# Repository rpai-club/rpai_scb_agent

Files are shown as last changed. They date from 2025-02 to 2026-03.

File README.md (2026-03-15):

# Cross Point Project
Software-Configured Breadboard Hardware Targeting Circuit Wiring Error Reduction in ECE Labs.
#
Abstract:
#
The hardware project aims to examine the effectiveness of software-configured wiring compared to traditional manual wiring of breadboards. While both methods use actual hardware, the software-configured approach automates the connections between components, thereby minimizing wiring errors and setup time. The intent is to investigate the impact of each approach on student comprehension, engagement, and error rates. By comparing these two approaches, the project seeks to determine which method better supports student engagement, educational outcomes and reduces frustration associated with complex circuit construction.
#
Introduction:
#
Hands-on experiential learning is a cornerstone of ECE education, typically relying on manual wiring of circuits on solderless breadboards. Using a traditional solderless breadboard as the means for building electronic circuit lab experiments requires the student, in addition to placing components, to manually insert wires to connect together the component pins according to a schematic diagram. These manual translation steps from schematic to hardware can lead to wiring errors in the experimental setup that can obscure circuit principles. While this manual wiring method offers valuable experience in physical component handling and troubleshooting, the extra time needed for debugging and correcting these errors leads to frustration and loss of precious lab time to investigate the circuit concept in question.

The goal is to evaluate the educational benefits and potential drawbacks of these software-configured hardware systems compared to traditional manual wiring. By doing so, it addresses the need for balancing hands-on skills with error minimization and conceptual understanding in electrical engineering education.
#
Analog switch matrix cross point experiment breadboard.
#
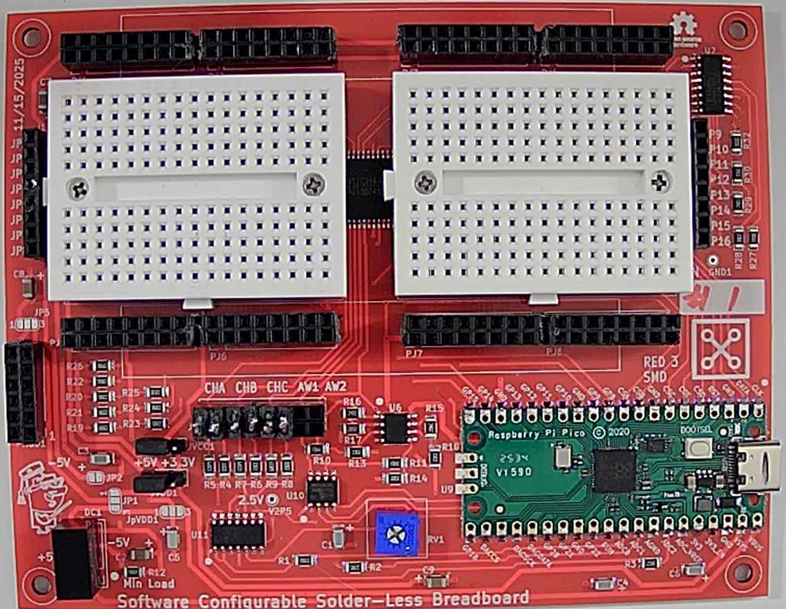
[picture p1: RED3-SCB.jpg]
Screenshot Prototype PCB

Production PCB (Red3 version, instructions for ordering boards can be found in PCB Projects folder)
 
The idea is to computerize the wiring of the breadboard in an effort to reduce student frustration when building complex experiments. Using four analog 16X8 cross point switches wired together into two 32X8 cross points with a fifth switch matrix interconnecting the two smaller arrays into effectively a single 64X16 array.

This breadboard makes real, hardware connections between the 64 breadboard component pins on the board to the16 “jumper” nodes on the board via software commands, instead of needing to manually install jumper wires. The prototype PCB is shown, figure 1, which incorporates two mini 170 pin solderless breadboards, one for each of the 32X8 cross point arrays. There are a combined 68 total component pin locations across both mini breadboards with power distribution strips top and bottom. The two mini breadboards connect to the PCB through pogo pins and so they can be easily removed. It would then be possible to bolt on custom daughter PCBs with whatever components are needed for a given course already installed. Such as CMOS transistor arrays (CD4007) with even some pre-wired sub-circuits like current sources and OTAs.

The combined 64X16 cross point matrix board uses a total of 5 CH446DS 16X8 analog cross point ICs (from China) programed via a RP-2040 micro controller breakout board (Pi Pico or equivalent). Materials cost per board, in quantities of 10 or more, is less than $30 not including the assembly labor.

The board is powered from the Pi Pico USB connection. For powering the experiment circuits, Jumpers can be configured for 0 and +3.3V, 0 and +5V or -5V and +5V power (or 0 and +10V) using an on board isolated 5V DC-DC generator.

LTspice is used to enter the schematic for the experiment. In addition to the standard library symbols a number of supporting schematic library files have been created. Schematic symbols for TO-92 transistors and resistors of various lead spacing are available in the LTspice files.

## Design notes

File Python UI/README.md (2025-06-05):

# Crosspoint Project interface for Universal-ALICE
Controling the Software Configurable Breadboard (SCB) hardware is built on top of the Universal ALICE hardware agnostic platform. 
#
Repository for the Python source code and hardware level specification files.
#
The main Universal ALICE GUI is written in Python (3.x) and depends only on the more or less generic standardly available Python plugin libraries (such as Tcl/Tk, numpy, pyplot etc.). The hardware specific interface level is also generally implemented in Python plus any plugin libraries (such as pyserial). The hardware specific interface for the SCB extends the Raspberry Pi Pico interface to include controls for reading LTspice .net or .cir formated netlists.

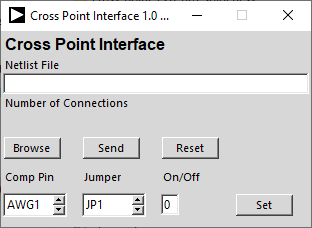
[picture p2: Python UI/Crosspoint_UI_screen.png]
Screenshot interfacescreen

Crosspoint Interface ALICE Screen

The Pi Pico board must be flashed with the corresponding firmware from the Arduino firmware folder.

If you are not a technical individual or highly familiar with computer operating systems and you have your choice of computers, a Windows computer is highly recommended. You will usually run into fewer issues, if any, with that operating system.

Known Issues: If your computer encrypts files saved on external storge devices (USB disk drives) then the UF2 Bootloader method of flashing firmware to micro-controller boards will not work. You would need to use a different computer that does not encrypt files or consult your local system administrator.

Linux Operating system: On Linux computers access to USB based serial comms devices may not be allowed for non root users by default. A udev rules file needs to be added. Place the 99-arduino.rules from this repository in etc/udev/rules.d

It contains one line per board / vendor:

SUBSYSTEMS=="usb", ATTRS{idVendor}=="2E8A", ATTRS{idProduct}=="000A", GROUP="dialout", MODE="0666"

If this rules file does not work on your version of Linux there may be other things like this that work. Searching the web on how to make serial USB devices work may provide an alternate solution or consult with your local Linux expert.

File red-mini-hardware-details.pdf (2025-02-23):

## Red Mini Hardware Construction (revised 1/20/25):

Analog switch matrix cross point experiment breadboard.

The idea is to computerize the wiring of the breadboard in an effort to reduce student frustration when building complex experiments. Using four analog 16X8 cross point switches wired together into two 32X8 cross points with a fifth switch matrix interconnecting the two smaller arrays into effectively a single 64X16 array.

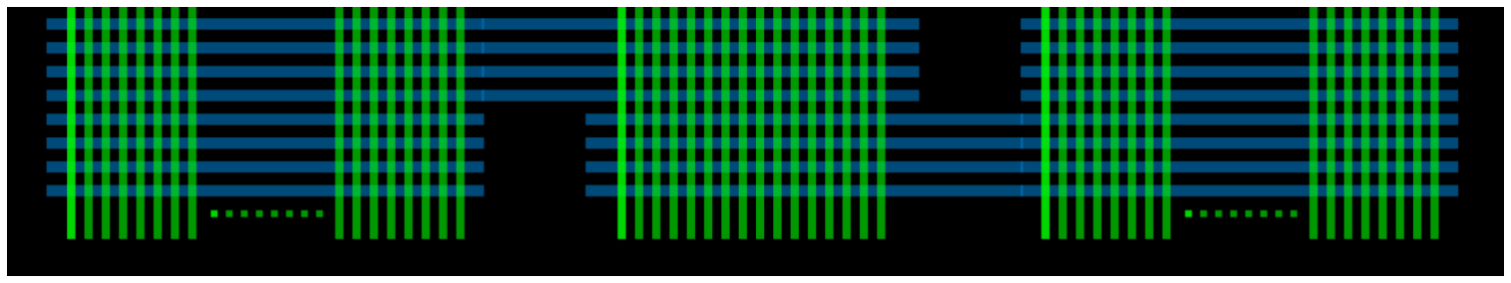
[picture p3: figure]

This breadboard makes real, hardware connections between the 64 breadboard component pins on the board to the16 “jumper” nodes on the board via software commands, instead of needing to manually install jumper wires. The prototype PCB is shown, figure 1, which incorporates two mini 170 pin solderless breadboards, one for each of the 32X8 cross point arrays. There are a combined 68 total component pin locations across both mini breadboards with power distribution strips top and bottom. The two mini breadboards connect to the PCB through pogo pins and so they can be easily removed. It would then be possible to bolt on custom daughter PCBs with whatever components are needed for a given course already installed. Such as CMOS transistor arrays (CD4007) with even some pre-wired sub-circuits like current sources and OTAs.

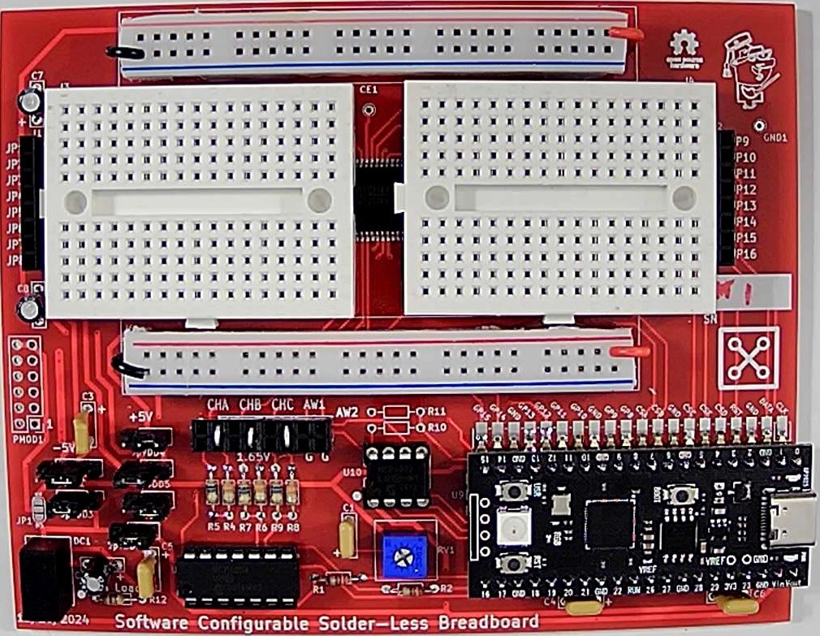
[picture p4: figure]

Figure 1, Prototype PCB.

The combined 64X16 cross point matrix board uses a total of 5 CH446DS [2] 16X8 analog cross point ICs (from China) programed via a RP-2040 micro controller breakout board (Pi Pico[3]
or equivalent).
Materials cost per board, in quantities of 10 or more, is less than $30 not including the assembly labor.

The board is powered from the Pi Pico USB connection. For powering the experiment circuits, male Pin Jumpers can be set for 0 and +3.3V, 0 and +5V or -5V and +5V power (or 0 and +10V) using an on board isolated 5V DC-DC generator.
LTspice[4]
is used to enter the schematic for the experiment. In addition to the standard library symbols a number of supporting schematic library files have been created, figure 2. Schematic symbols for TO-92 transistors and resistors of various lead spacing have been created. There are also example schematic symbols with the proper pin spacing for 8, 14 and 16 pin DIP packages. The standard library components can of course also be used.

The library schematics for the switch matrix connections contain 60 Ω resistors and 16 pF capacitors which model the analog switch. One end of a matrix switch will have the component pin net and the other end will have one of the 16 "jumper" nets (JP1-16).

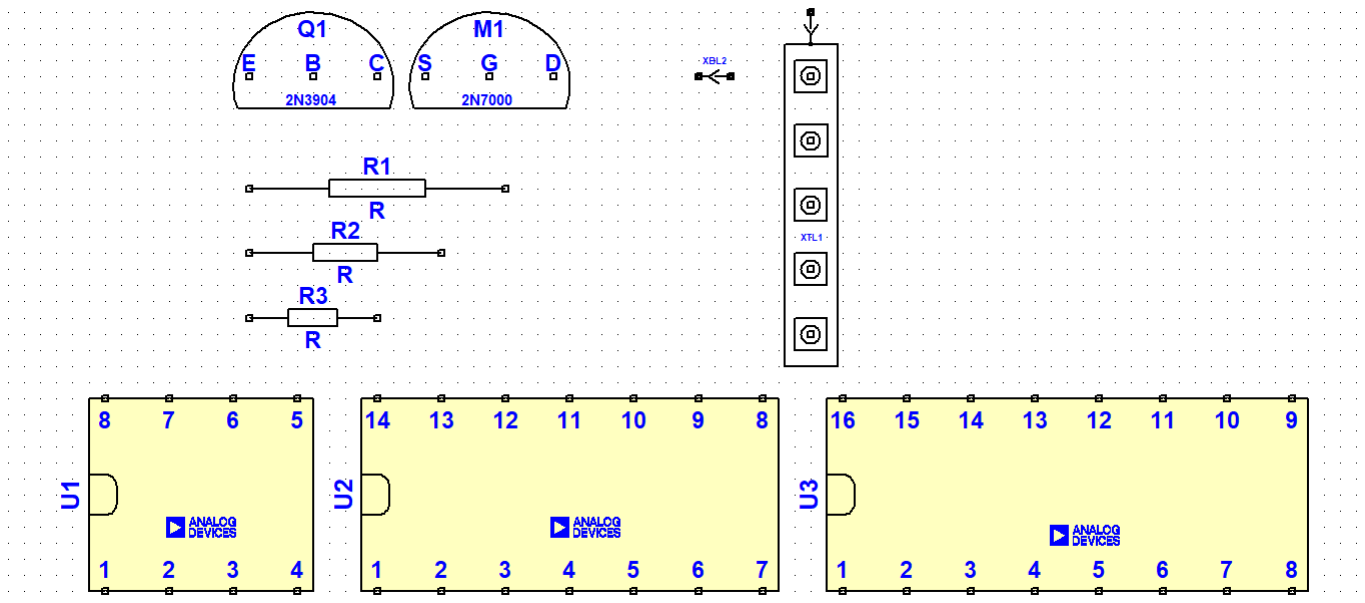
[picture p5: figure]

Figure 2, Schematic symbols.

A floor planning schematic template, figure 3, has been created to help the user figure out where to place the parts on the left and right side mini breadboards and then use the "jumpers" to wire them together. There is a schematic symbol for each breadboard column (the 5 pins shorted together). Each breadboard column has a specific name based on its location. Names are numbered from 1 to 17 starting with the top left section, TL1-17, then the bottom left section, BL1-17, then the top right section TR1-17, and finally the bottom right section, BR1-17.

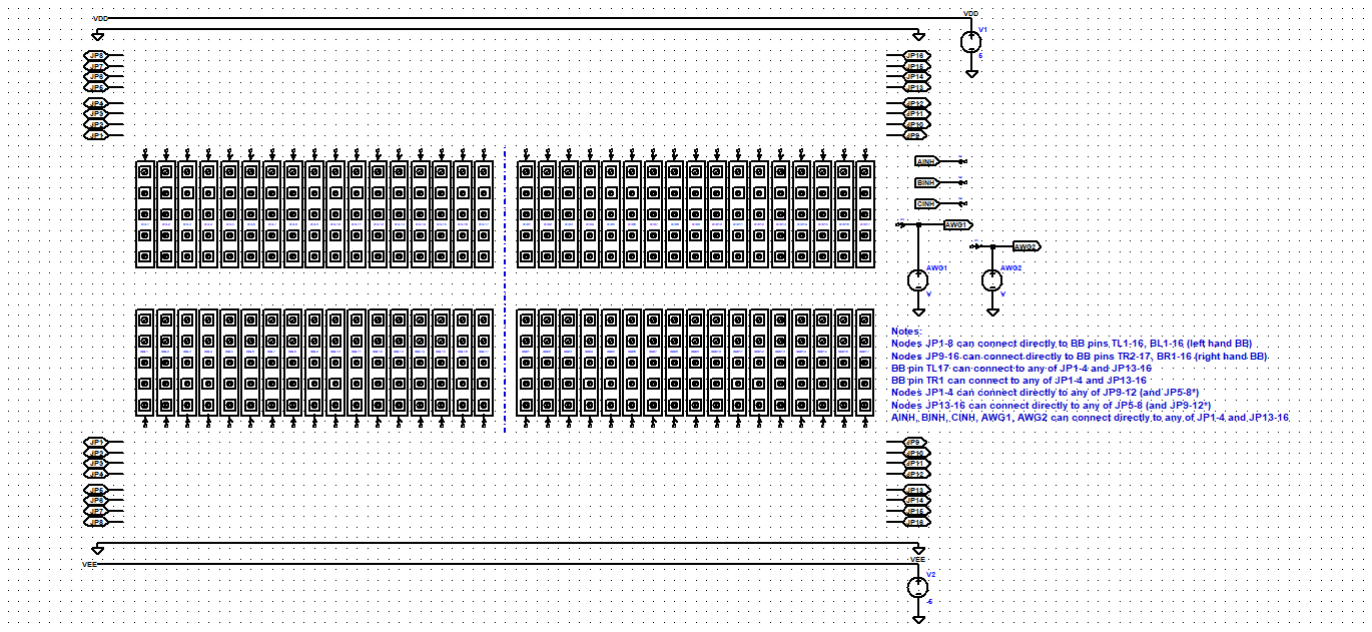
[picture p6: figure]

Figure 3, LTspice floor planner template schematic

In figure 4 we see an example circuit of a transistor level op-amp that has been floorplanned and interconnected with the JP jumper nets. Components can also be connected between a column pin and one of the top and bottom power and ground rails simply by a wire.

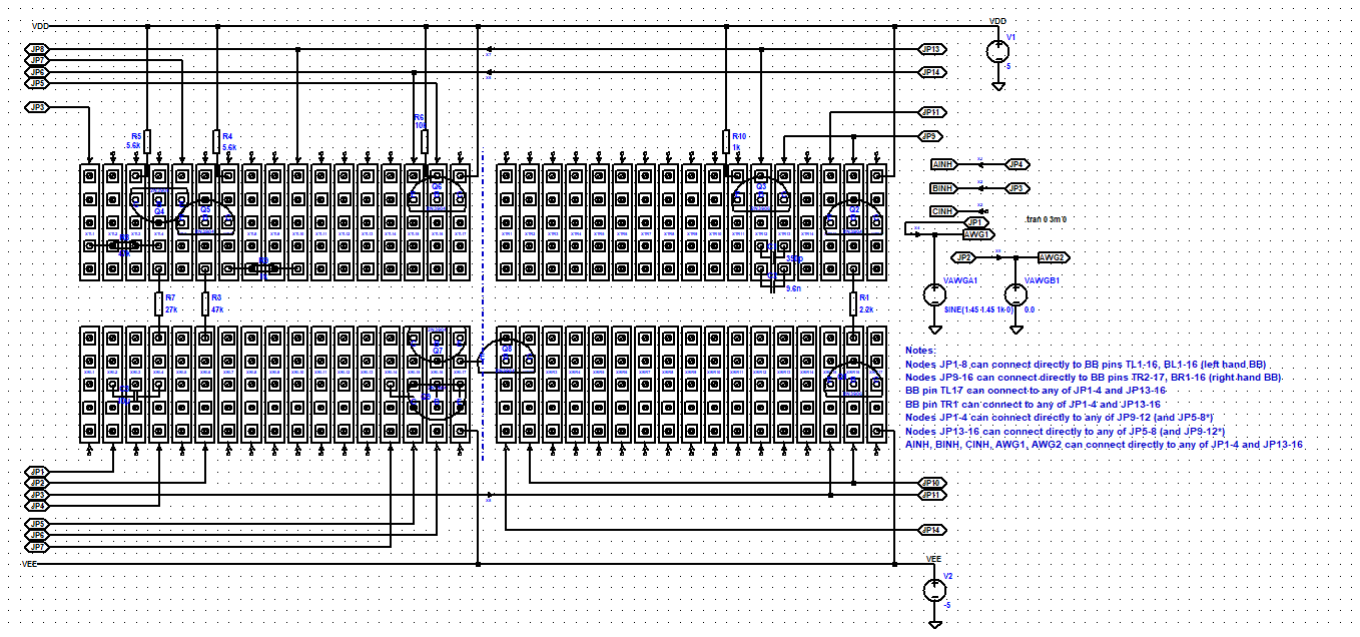
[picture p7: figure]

Figure 4, Example floor planned circuit

There is also a way to draw the circuit as a more conventional schematic, figure 5. The same op-amp circuit has been redrawn using standard symbols from the LTspice library with the addition of single switch interconnection symbols. The little pointy arrow symbols are placed in series with certain nets to indicate the component locations on the breadboard. These interconnection symbols are again named based on the BB holes (TL1-17, BL1-17, TR1-17, BR1-17) the parts are plugged into. This approach is easier to visualize the circuit as a schematic but perhaps harder to floor plan where to place the devices.

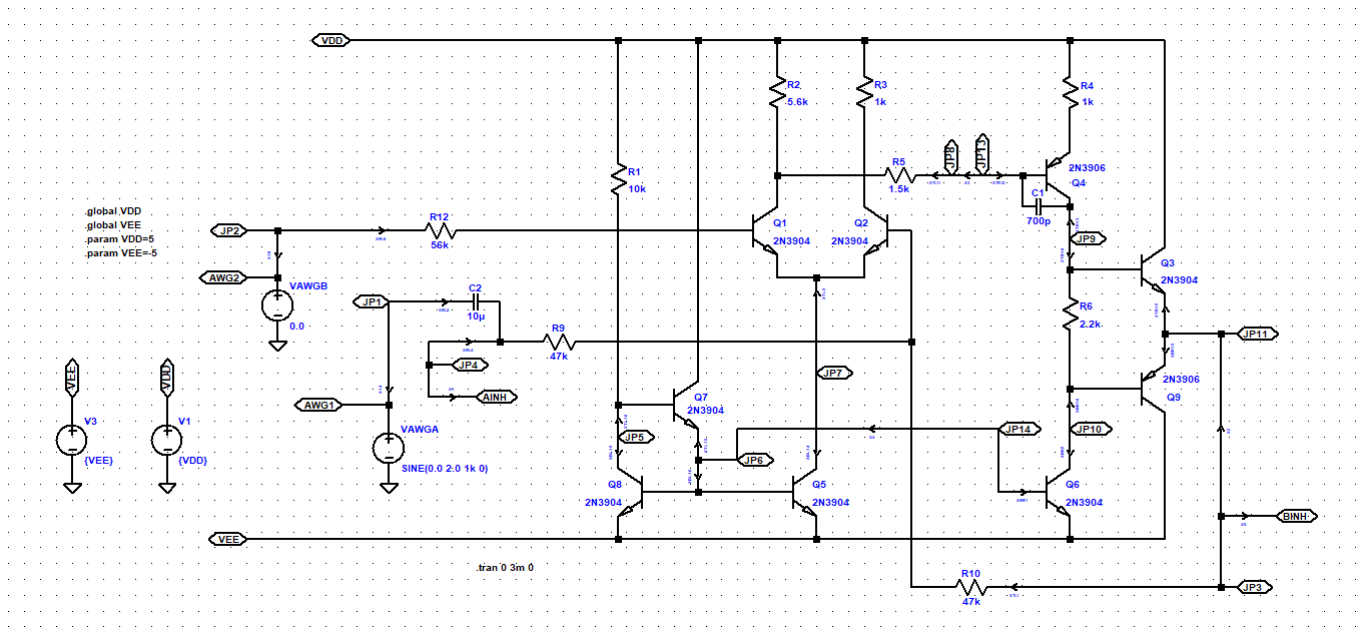
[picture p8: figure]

Figure 5, Conventional Schematic method

Correct simulation results insure that you have it all wired correctly before moving to the actual hardware.

A Python script looks through the saved LTspice .cir net list file looking for sub circuits starting with XX in their names. Then parses the connections based on the names (based on breadboard pin locations, TL1-17, BL1-17, TR1-17, BR1-17) and JP1-16 to send commands to the Pi Pico and on to the cross point switches. Everything else is ignored.

As long as you follow these rules when building the schematic the process is simple and mostly automatic. Programming the board is done through ALICE Universal[5]
using a hardware specific
interface configuration file for this cross point prototype including a way to turn on and off matrix switches manually as well.

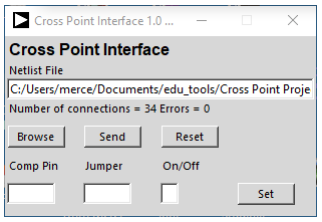
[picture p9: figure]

Cross Point Matrix control user interface The following are a few additional example circuits built using the breadboard.
The LTspice schematic in figure 6 was used to configure four CD4007 transistor arrays as a ring oscillator consisting of 11 CMOS inverter stages. It uses 56 of the 68 possible device pins and all 16 of the jumpers of the switch matrix. Manual jumper wires are used to connect each of the DIP (pins 7 and 14) ground and power pins to the power and ground rails on the board. All other connections are programed by the netlist.

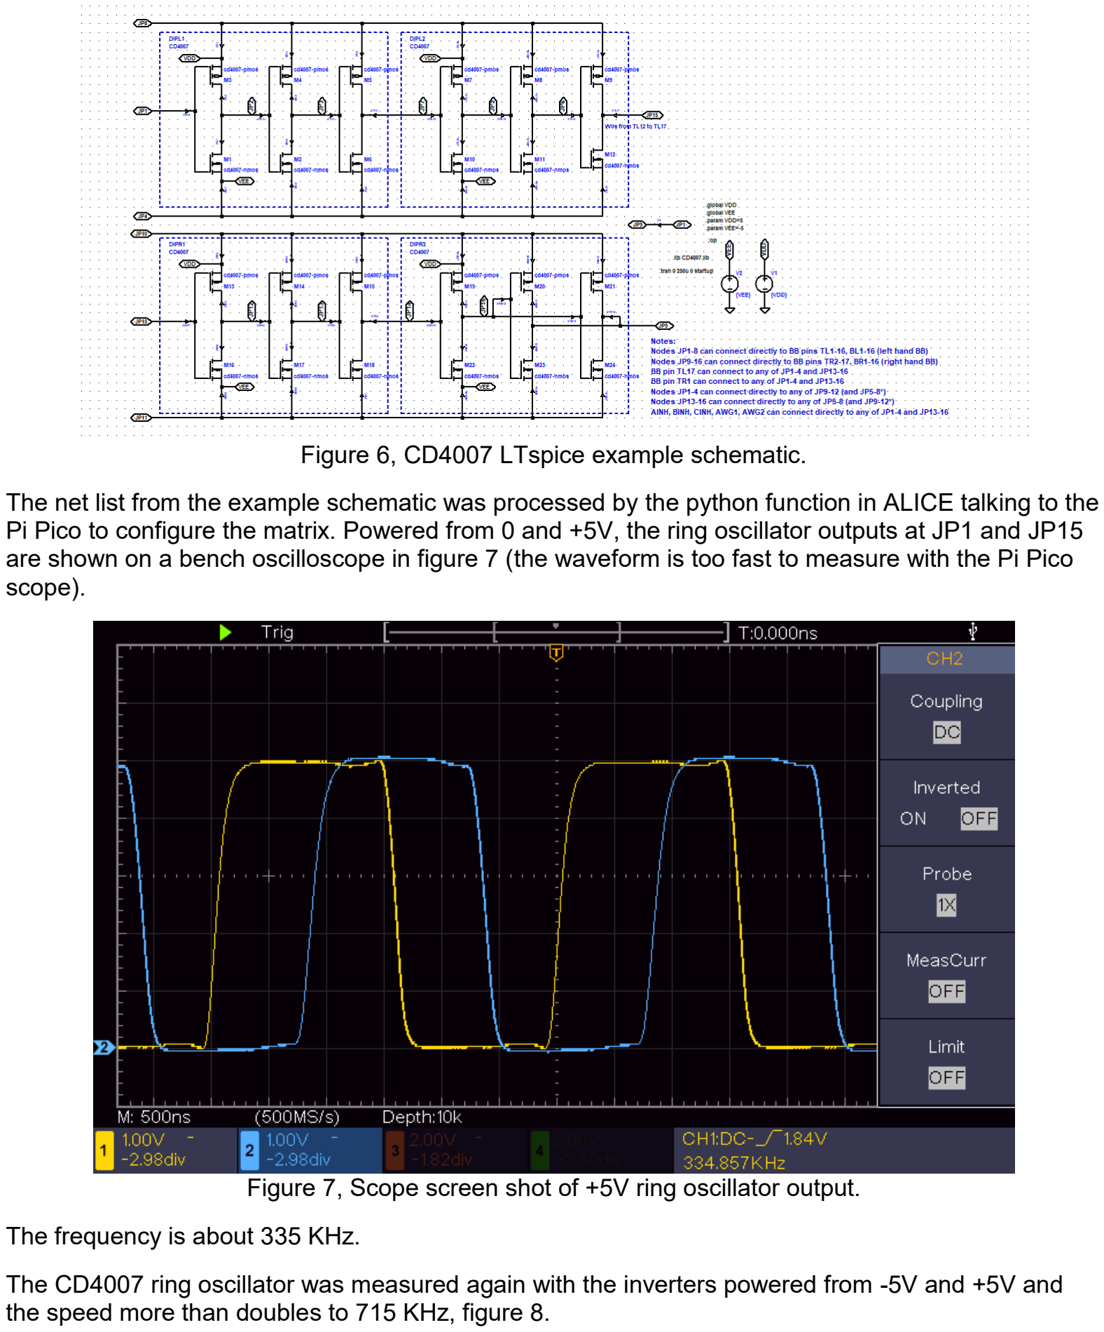
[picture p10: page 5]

Figure 6, CD4007 LTspice example schematic.

The net list from the example schematic was processed by the python function in ALICE talking to the Pi Pico to configure the matrix. Powered from 0 and +5V, the ring oscillator outputs at JP1 and JP15 are shown on a bench oscilloscope in figure 7 (the waveform is too fast to measure with the Pi Pico scope).

Figure 7, Scope screen shot of +5V ring oscillator output.

The frequency is about 335 KHz.

The CD4007 ring oscillator was measured again with the inverters powered from -5V and +5V and the speed more than doubles to 715 KHz, figure 8.

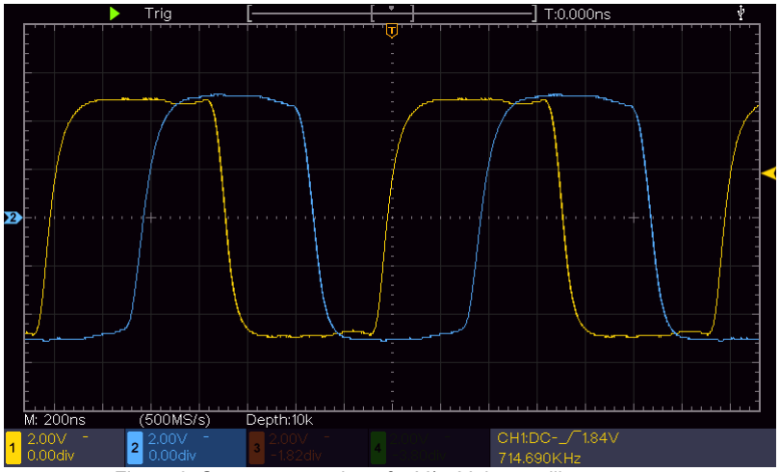
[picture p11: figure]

Figure 8, Scope screen shot of -5V/+5V ring oscillator output.

A Schmitt trigger relaxation oscillator can be constructed from the CD4007 CMOS transistor level inverters, figure 9. The Schmitt trigger is made by rearranging the connections and adding resistor R1 and Capacitor C1 to set the frequency. The M1,3 and M7,10 inverters are stronger than the other 4 inverters because their sources are connected directly to VDD and VEE rather than through the 60 Ω switch resistances. A “strong” inverter and a “weak” inverter are connected as a latch. This latch action determines the high and low threshold of the Schmitt trigger.

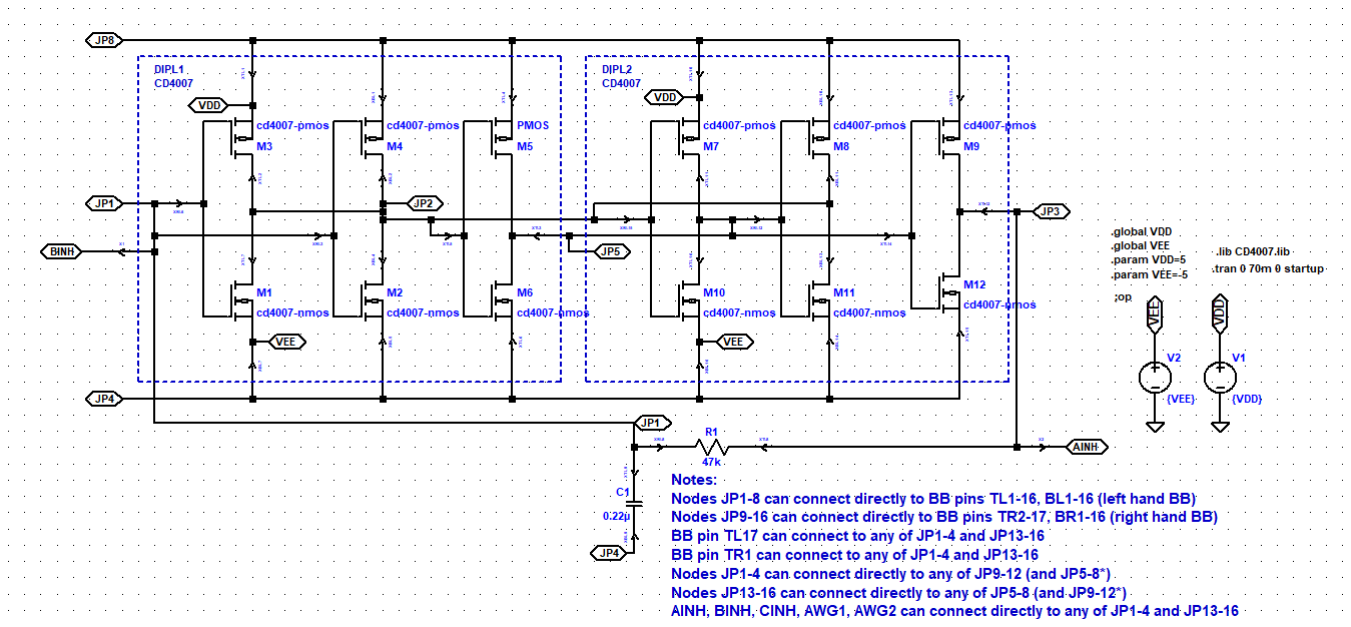
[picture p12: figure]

Figure 9, CMOS inverter relaxation oscillator.

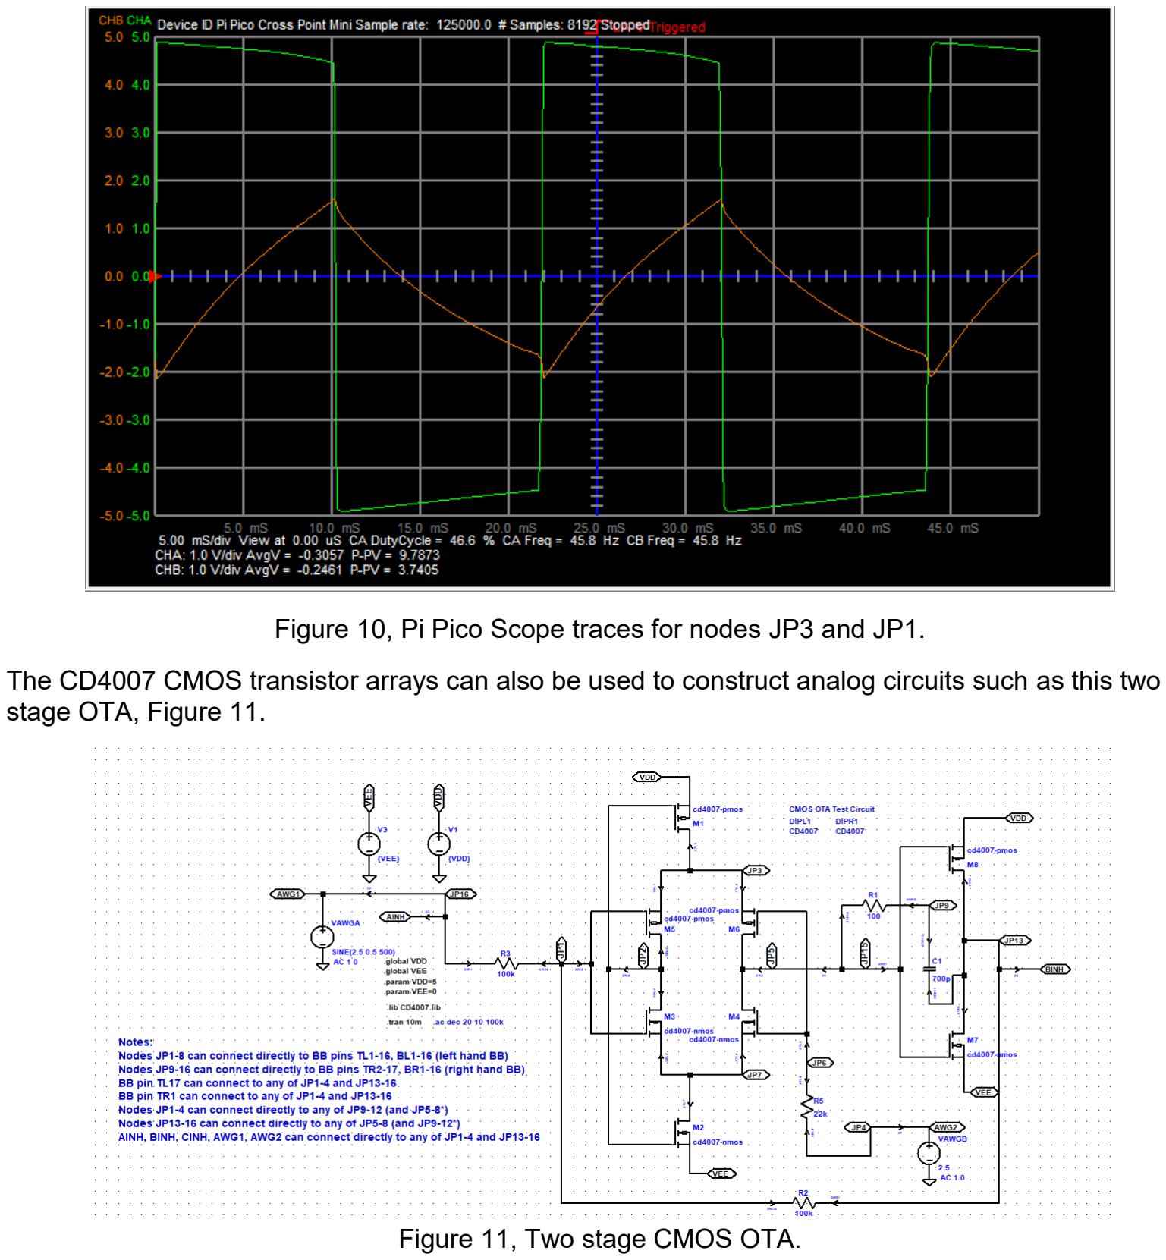
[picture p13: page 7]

Figure 10, Pi Pico Scope traces for nodes JP3 and JP1.

The CD4007 CMOS transistor arrays can also be used to construct analog circuits such as this two stage OTA, Figure 11.

Figure 11, Two stage CMOS OTA.

References:

[1] Jumperless breadboard product, https://www.tindie.com/products/architeuthisflux/jumperless/ , https://github.com/Architeuthis-Flux/Jumperless
[2] CH446DS1 datasheet, https://www.wch-ic.com/downloads/CH446DS1_PDF.html
[3] Pi Pico, https://www.digikey.com/en/products/detail/raspberry-pi/SC0915/13684020?utm_adgroup=&gad_source=1 (https://www.digikey.com/en/products/detail/raspberry-pi/SC0915/13684020?utm_adgroup=&gad_source=1)
[4] LTspice, https://www.analog.com/en/resources/design-tools-and-calculators/ltspice-simulator.html
[5] ALICE Universal, https://github.com/damercer/Universal-ALICE

Construction order of operations:

The order of assembly operations is first to install all the components that are soldered using hot air.

The first things requiring solder paste and hot air to install on the board are the pogo pins. Add a small dollop of solder paste in each pogo pin hole. Then insert a pogo pin (spring end up) in each hole. Using hot air reflow the solder paste until each pin flows down level into its hole.

The second things to install are the CH446DS quad flat pack ICs. Apply a small amount of solder paste along the four sides of the footprint. Using a conventional soldering iron melt the solder paste and “tin” the PCB lands with small mounds of fresh solder. The correct amount of solder will generally be left behind on each pin as the soldering iron is slowly dragged across the PCB.

Note the small white dot on the PCB near the lower left of each footprint on the PCB. This needs to be aligned with the dot on the IC package. It is a good idea to have all five of the packages properly aligned / orientated before hand. Mount the ICs one at a time. Using the hot air heat each IC footprint until the solder starts to melt. Using tweezers pick up the IC package, remembering to keep the proper orientation with the white dot, and place it on the melted solder. The IC should self-align and float on the melted solder by surface tension. You may need to nudge the IC slightly with the tweezers depending on how close it was to the proper position when you placed it. Remove the hot air as soon as it looks aligned properly to not over heat the IC.

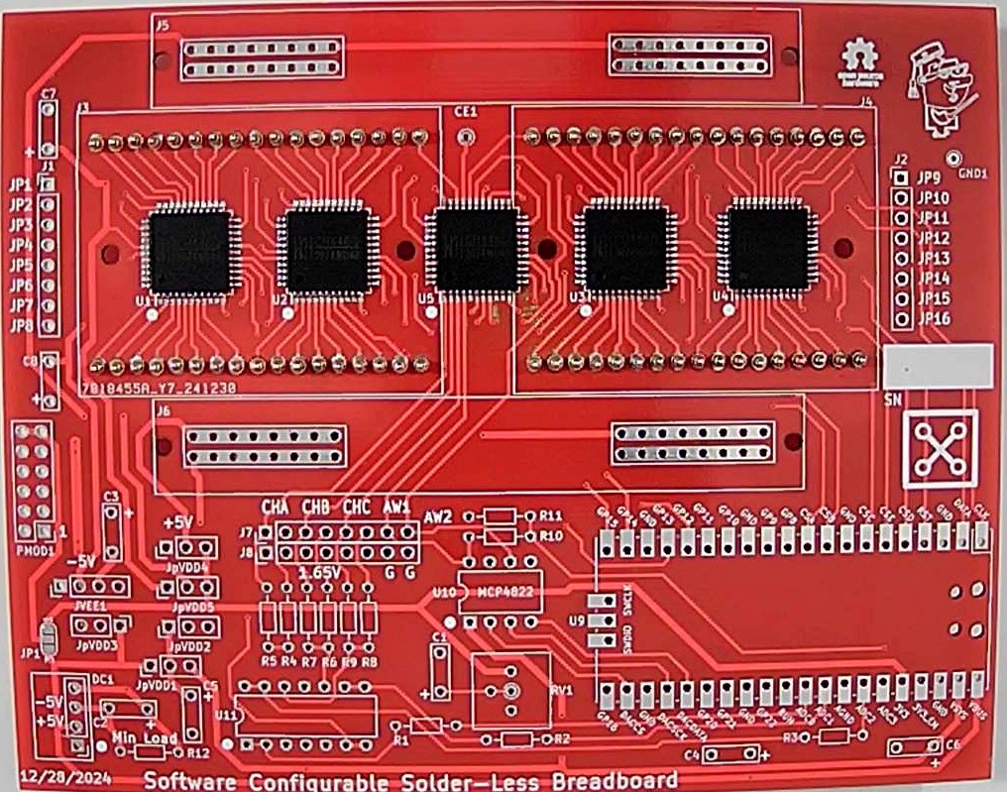
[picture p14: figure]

When installing the rest of the components which are through hole, it is best to start with the shortest devices (closest to the surface of the board). These would be the resistors. Then move to the next tallest etc. A small strip of masking tape can be used to temporarily hold the components tight to the board when you flip the board over to solder the leads from the bottom.

Additional Notes:

Software Configurable Solderless Breadboard Connections

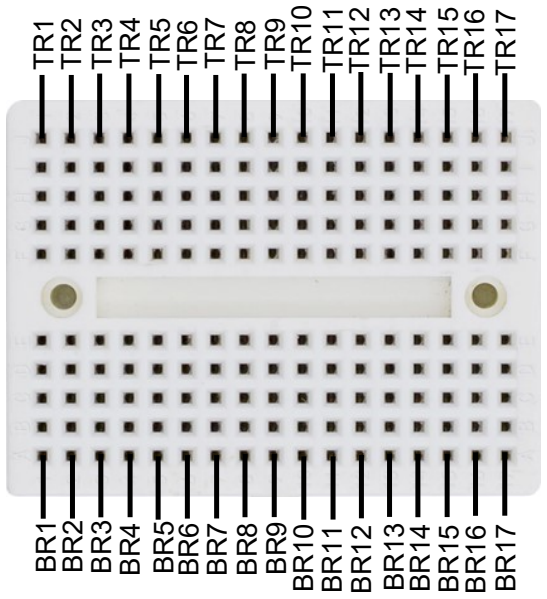
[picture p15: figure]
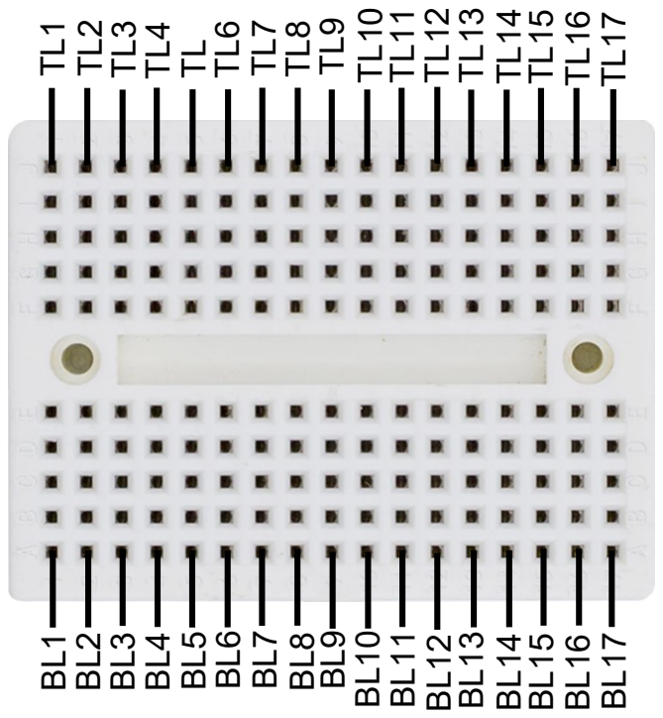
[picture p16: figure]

Mini Solderless Breadboard Pin Names (Red)

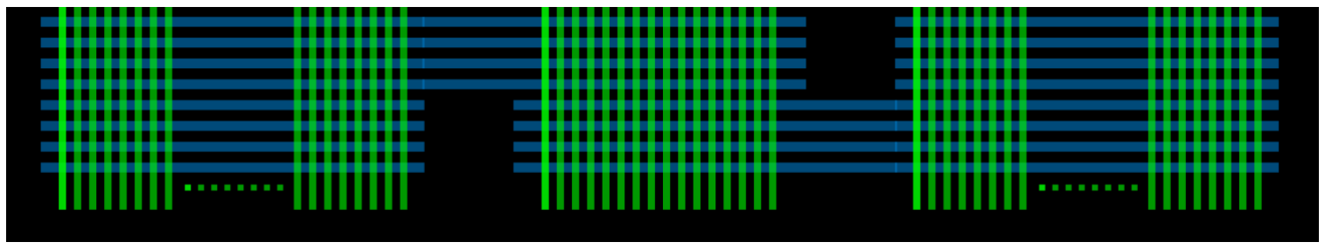
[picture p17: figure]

Notes:

Switch Nodes JP1-8 can connect directly to BB pins TL1-16, BL1-16 (left hand BB) Switch Nodes JP9-16 can connect directly to BB pins TR2-17, BR1-16 (right hand BB) BB pin TL17 can connect to any of JP1-4 and JP13-16
BB pin TR1 can connect to any of JP1-4 and JP13-16
Switch Nodes JP1-4 can connect directly to any of JP9-12 (and JP5-8*)
Switch Nodes JP13-16 can connect directly to any of JP5-8 (and JP9-12*)
AINH, BINH, CINH, AWG1, AWG2 can connect directly to any of JP1-4 and JP13-16

BL17 and BR17 normally default as open circuit but can be optionally connected to -5 V power rail using solder jumpers marked JP3 and JP4 on the underside of the board. TL1 TL2 BL1 BL2 TL3 BL3 TL

BL5

TL6

TL7

TL9

TL10
TL11

BL6
BL7

BL9

BL10
BL11

TL13
TL14
TL15

BL13
BL14
BL15

TR2
TR3

TR4
TR6

TR7
TR8

TR10
TR11
TR12

TR14

TR15
TR16

BR2
BR3
BR4
BR6

BR7

BR8
BR10
BR11
BR12

BR14
BR15
BR16

BR5
BR13

Power Rail Jumper Configuration:

The standard Pi Pico pinout has two possible positive voltages supplied from the USB port. The VBUS pin is directly connected to the USB connector +5V. The VSYS pin has a diode in series with USB connector +5V. The board has 6 jumper locations that are used to configure and distribute voltages on the board. The analog switches are powered from the VDD1 positive voltage trace (+5V) and VEE1 negative voltage trace (-5V). How VDD1 and VEE1 are configured is determined by how the jumpers are shorted.

Jumper jpVDD1 (see picture below) is a three pin jumper where the center pin can be shorted to either the left or right pin. Installing a short between center and left pin connects VDD1 to VBUS. Installing a short between center and right pin connects VDD1 to VSYS.

The on board isolated DC/DC converter is powered directly from the VBUS pin. The isolated 5V output can be connected two ways using Jumpers jpVDD2 and jpVDD3. The positive output terminal on the center pin of jpVDD2 can be connected to ground by shoring it to the right pin (GND) or the VDD1 trace by shorting it to the left pin. When the positive output terminal is connected to ground the output negative terminal becomes -5V with respect to ground and is connected to the center pin of jumper jpVDD3. This -5V can be connected to VEE1 by shorting the center pin to the left pin.

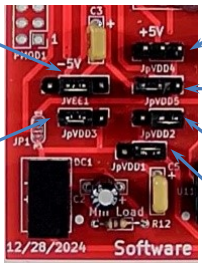
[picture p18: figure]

The board has four power distribution rails. Two on the top and two on the bottom. The lower of the two top power rails is always connected to GND. The pins of jumper jpVDD5 determine what voltage supplies the upper half of the top rail. The center pin of jpVDD5 is connected to the upper half of the top rail. Shorting the left pin to the center connects to VDD1 and shorting the right pin to the center connects to the +3.3V supplied by the Pi Pico on board LDO.

Four pin jumper jVEE1 determines the voltage supplied to the lower of the two bottom power rails. Shorting the two center pins connects it to the VEE1 (generally -5V). Three pin jumper jpVDD4 determines the voltage supplied to the upper of the two bottom power rails. Shorting the left pin to center pin connects to GND. Shorting the right pin to center pin connects to +3.3V.

jpVDD1
Right to connect to VSYS
Left to connect to VBUS

jpVDD2
Right to connect to GND

jpVDD3
Left to connect to GND

jVEE1
Short center two pins

jpVDD4
Left to connect to GND
Right to connect to +3.3V
jpVDD5
Left to connect to VDD1
Right to connect to +3.3V

Pi Pico Black with 4 MB flash and Type C USB modifications:

This Black clone of the Pi Pico has some interesting differences between it and the standard (Green) Pi Pico.

First is, it provides access to the ADC3 mux input.

The second difference is how Power pins (40 and 39 lower right) are arranged with respect to the power supplied from the USB connector. Note the two pictures below. A short needs to be added to the Black boards.

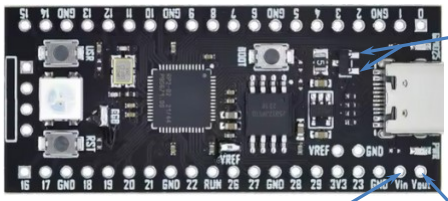
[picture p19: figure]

Solder a short across
these two pins.

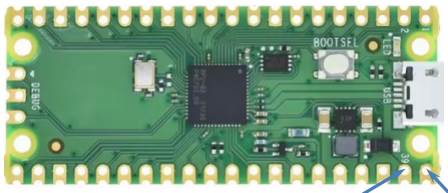
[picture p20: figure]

Full USB voltage appears
on this Pin.

Normally this pin is use to apply external power onto board. With short added full USB voltage now comes out on this Pin.

USB voltage less one
diode drop appears on
this Pin.

USB voltage less one
diode drop appears on
this Pin rather than the
full USB voltage.

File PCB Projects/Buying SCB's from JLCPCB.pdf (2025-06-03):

## Step 1: Create an order

Navigate to JLCPCB (https://jlcpcb.com/?from=VGSU&gad_source=1&gad_campaignid=14179457750&gbraid=0AAAAABS1QqkVs0kspxxTUOpfzXbQFzQwS) and make a free account if you do not have one

Select “Order Now” in the top right of your screen

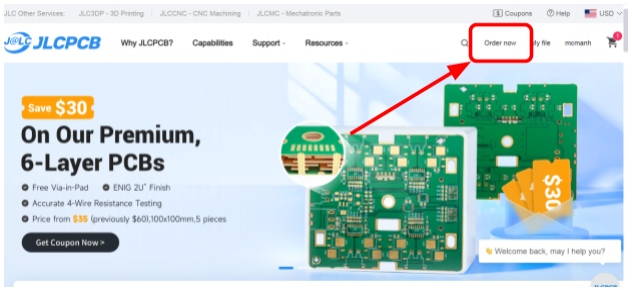
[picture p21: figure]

## Step 2: Upload Gerber

Click “Add Gerber File” in the middle of the screen

Navigate to your Cross Point Project (https://github.com/damercer/Cross-Point-Project) repository or clone it (https://www.notion.so/Making-Doug-s-Solderless-Breadboard-1a20f9dca44b80c89d19c69c578b6200?pvs=21) if you do not already have it, or alternatively follow the direct links in each step where a file is required

- Navigate to the zip file
Cross-Point-Project→PCB Projects→cross-point-exp-brd-mini-red2-sjmp →Gerbers→cross-point-exp-brd-mini-red2-sjmp.zip

OR

- Download zip directly
Follow this link (https://github.com/damercer/Cross-Point-Project/blob/main/PCB%20Projects/cross-point-exp-brd-mini-red2-sjmp/Gerbers/cross-point-exp-brd-mini-red2-sjmp.zip)
Press “view raw” to download

Select and upload the zip file

## Step 3: Select Build Specifications

The specifications are the defaults from JLCPBC with the following changes:

- PCB color RED
- PCB assembly ON
- PCBA type STANDARD
- Confirm Parts Placement YES (will have a pop up menu, check the box for “Do not confirm automatically”)

Price should be $9.40 at this point. Press “Next” below calculated price

Specification images:

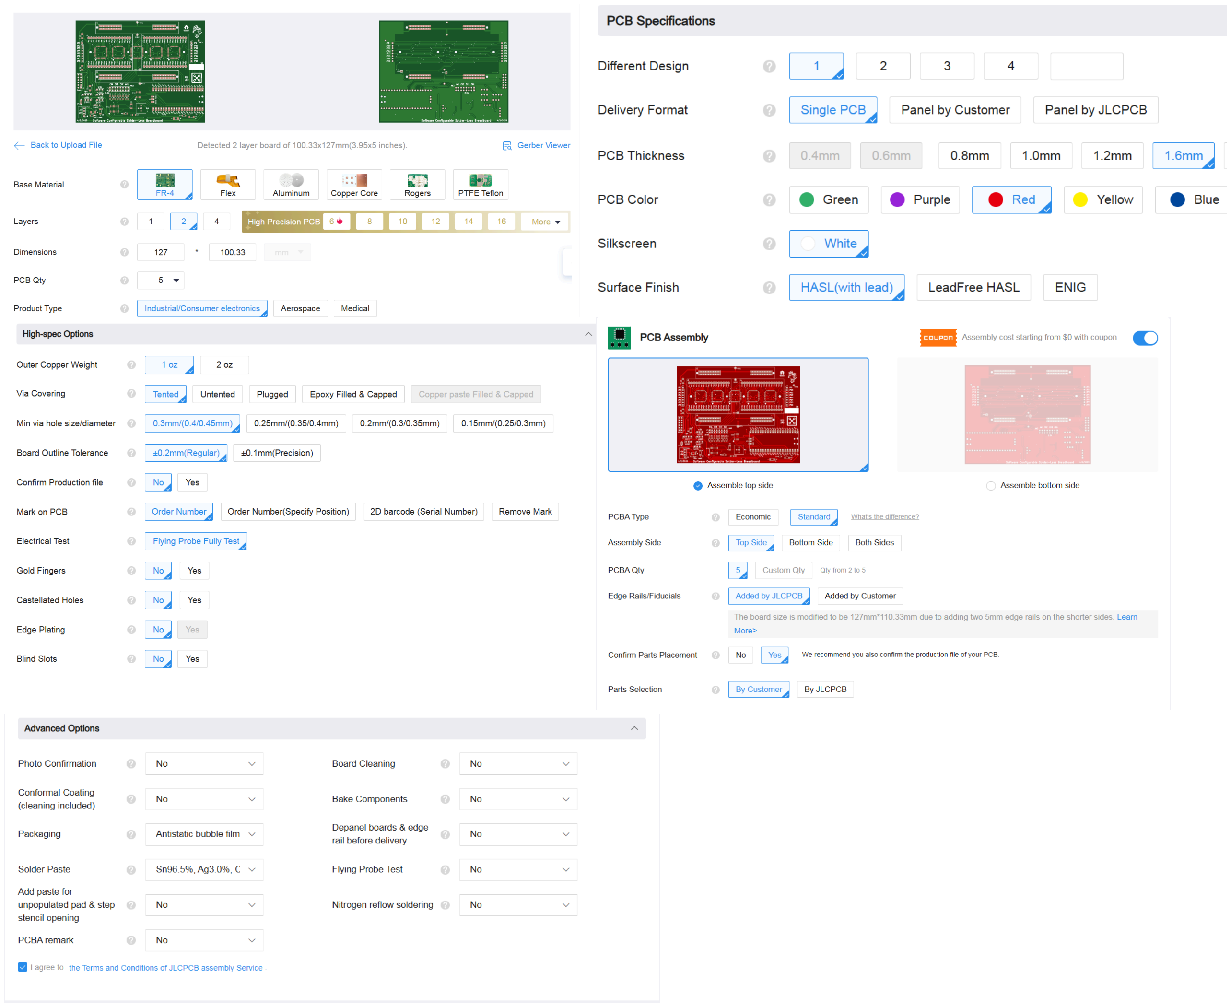
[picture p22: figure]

## Step 4: Confirm Board Image

Top of Board | Bottom of Board

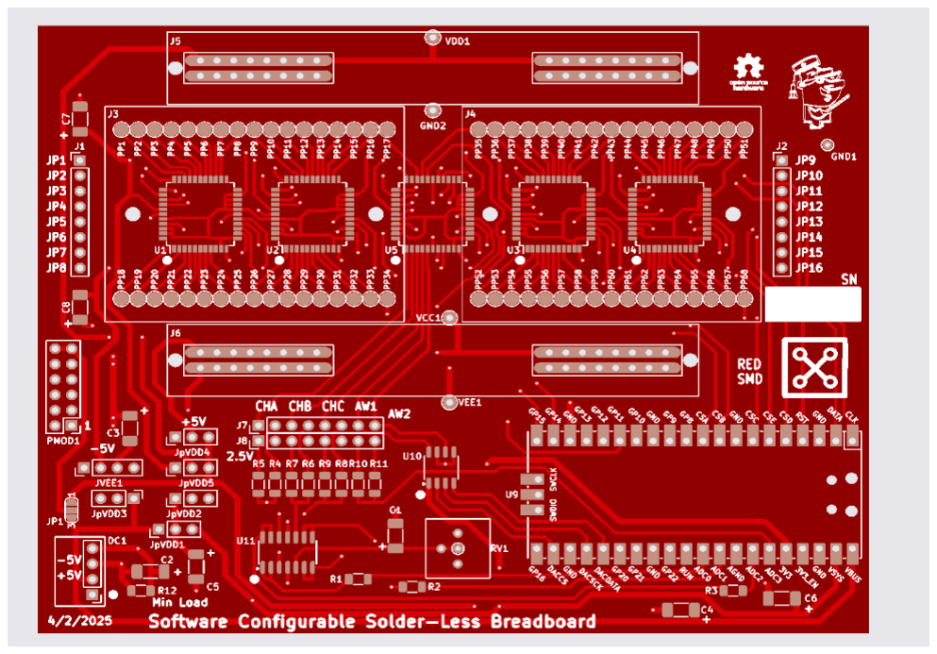
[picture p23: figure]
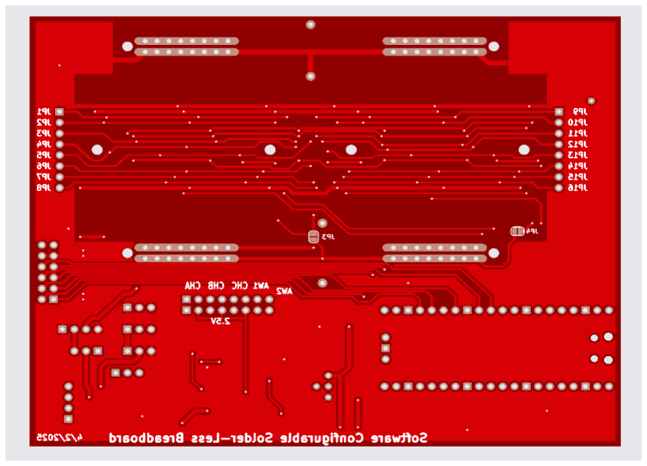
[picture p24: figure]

Confirm that your board matches with these images and select “NEXT”

## Step 5: Upload BOM and CPL files

NOTE: It is possible that the sheets contain extra, blank pages. If there are any delete them as the upload will fail if these files have multiple sheets

## BOM

Navigate to BOM:
Cross-Point-Project → PCB Projects → cross-point-exp-brd-mini-red2-sjmp → JLCPCB_BOM_RED2_SMD.xlsx

OR
Directly download BOM:
Follow this link (https://github.com/damercer/Cross-Point-Project/blob/main/PCB%20Projects/cross-point-exp-brd-mini-red2-sjmp/JLCPCB_BOM_RED2_SMD.xlsx) and press “view raw” to download

## CPL

Navigate to CPL:
Cross-Point-Project → PCB Projects → cross-point-exp-brd-mini-red2-sjmp → JLCPCB-red2-sjmp-top-pos.csv
OR

Directly download CPL:
Follow this link (https://github.com/damercer/Cross-Point-Project/blob/main/PCB%20Projects/cross-point-exp-brd-mini-red2-sjmp/JLCPCB-red2-sjmp-top-pos.csv) and press “download raw file

Click “Process BOM and CPL” which may take a few attempts to be accepted

## Step 6:Confirm BOM

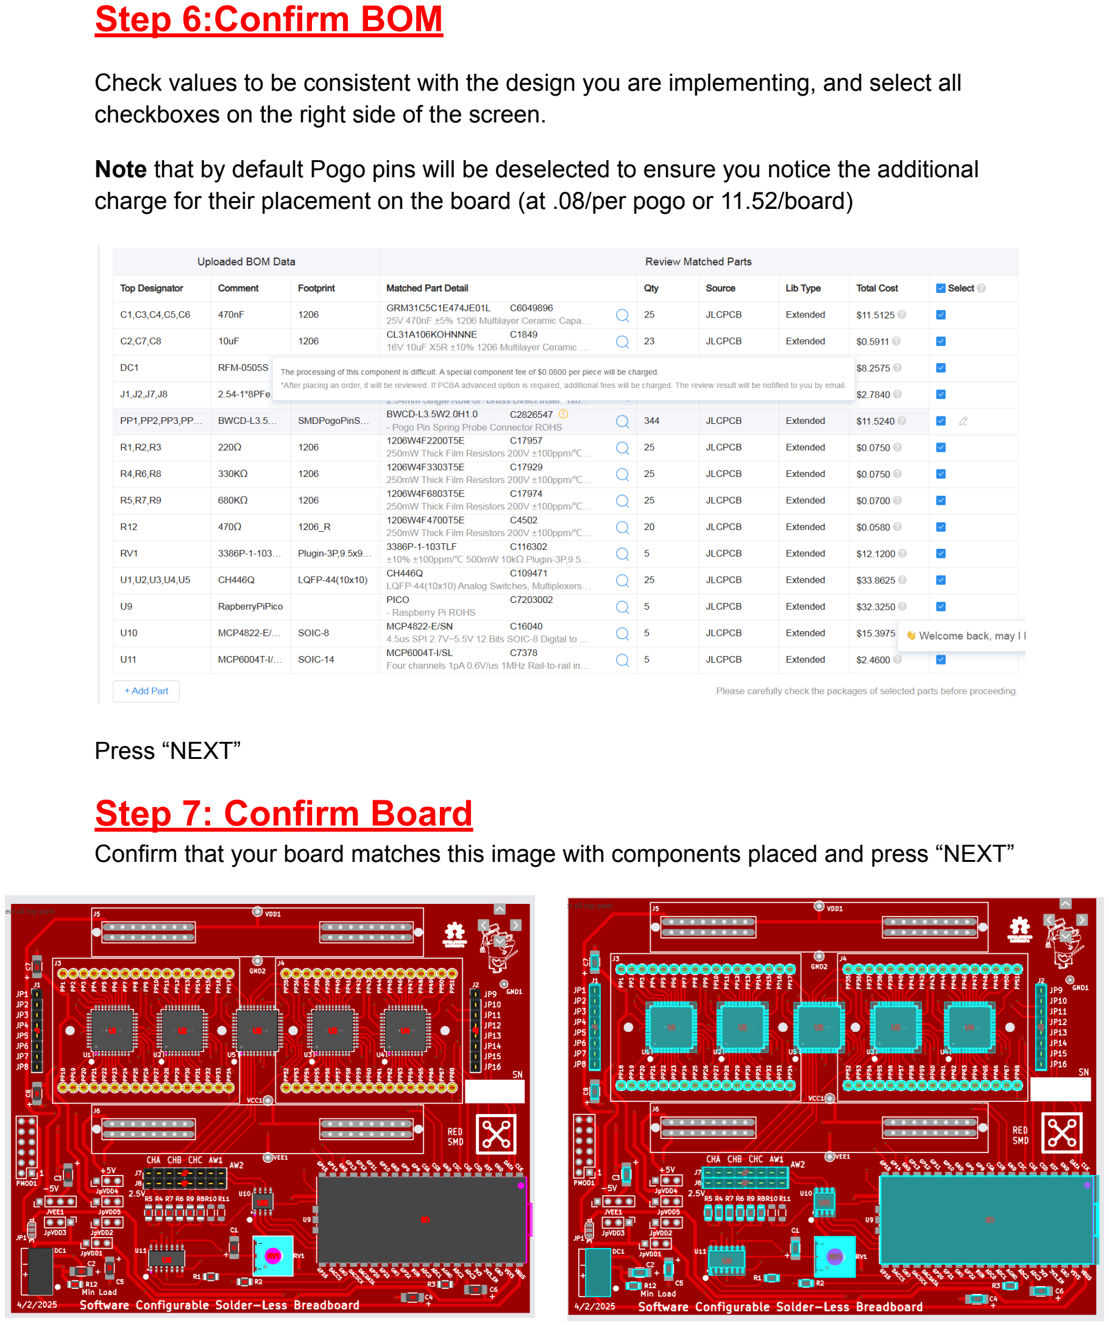
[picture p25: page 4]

Check values to be consistent with the design you are implementing, and select all checkboxes on the right side of the screen.

Note that by default Pogo pins will be deselected to ensure you notice the additional charge for their placement on the board (at .08/per pogo or 11.52/board)

Press “NEXT”

## Step 7: Confirm Board

Confirm that your board matches this image with components placed and press “NEXT”

## Step 9: Confirm Order

On the next screen you will see a bill for all materials and engineering for 5 boards, the total price in the top right should read $228.14, with a product weight of 1.47kg

Note that you can pay a surcharge for expedited assembly, which will increase price

To check out you must select a product description, this one seems like the most apt description, however I am unsure if this decision affects the order


Select “Save to cart” and follow checkout instructions to place order

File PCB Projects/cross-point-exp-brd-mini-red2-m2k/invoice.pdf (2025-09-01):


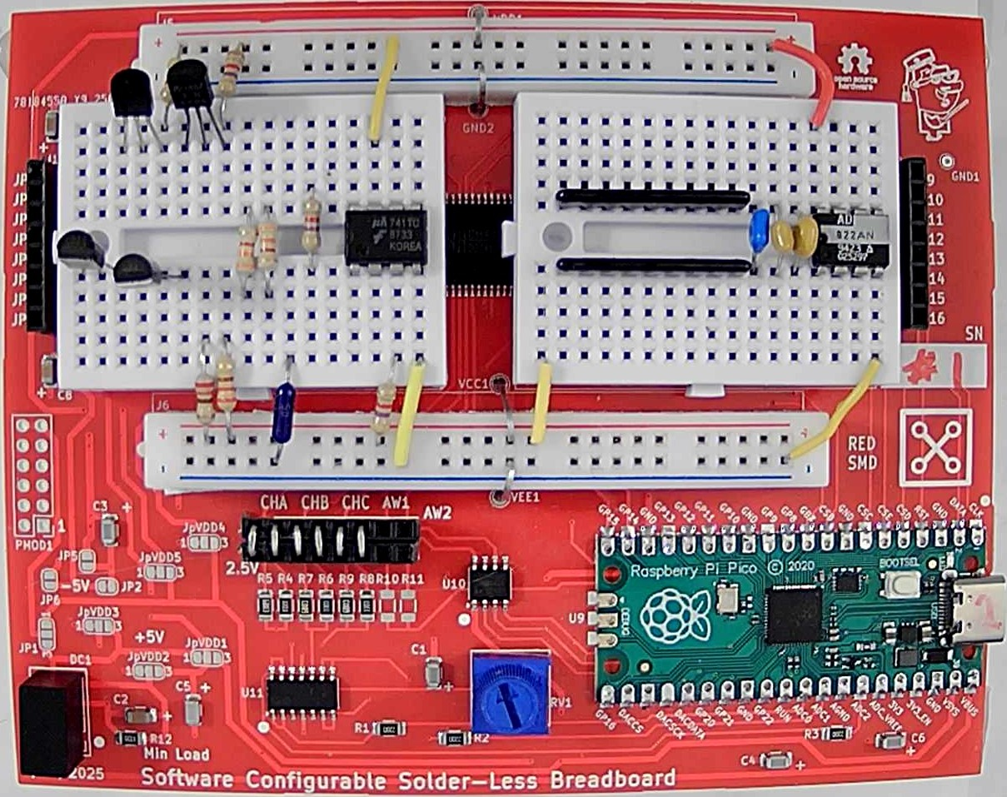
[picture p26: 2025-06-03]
Red1-Board-smd-production.png

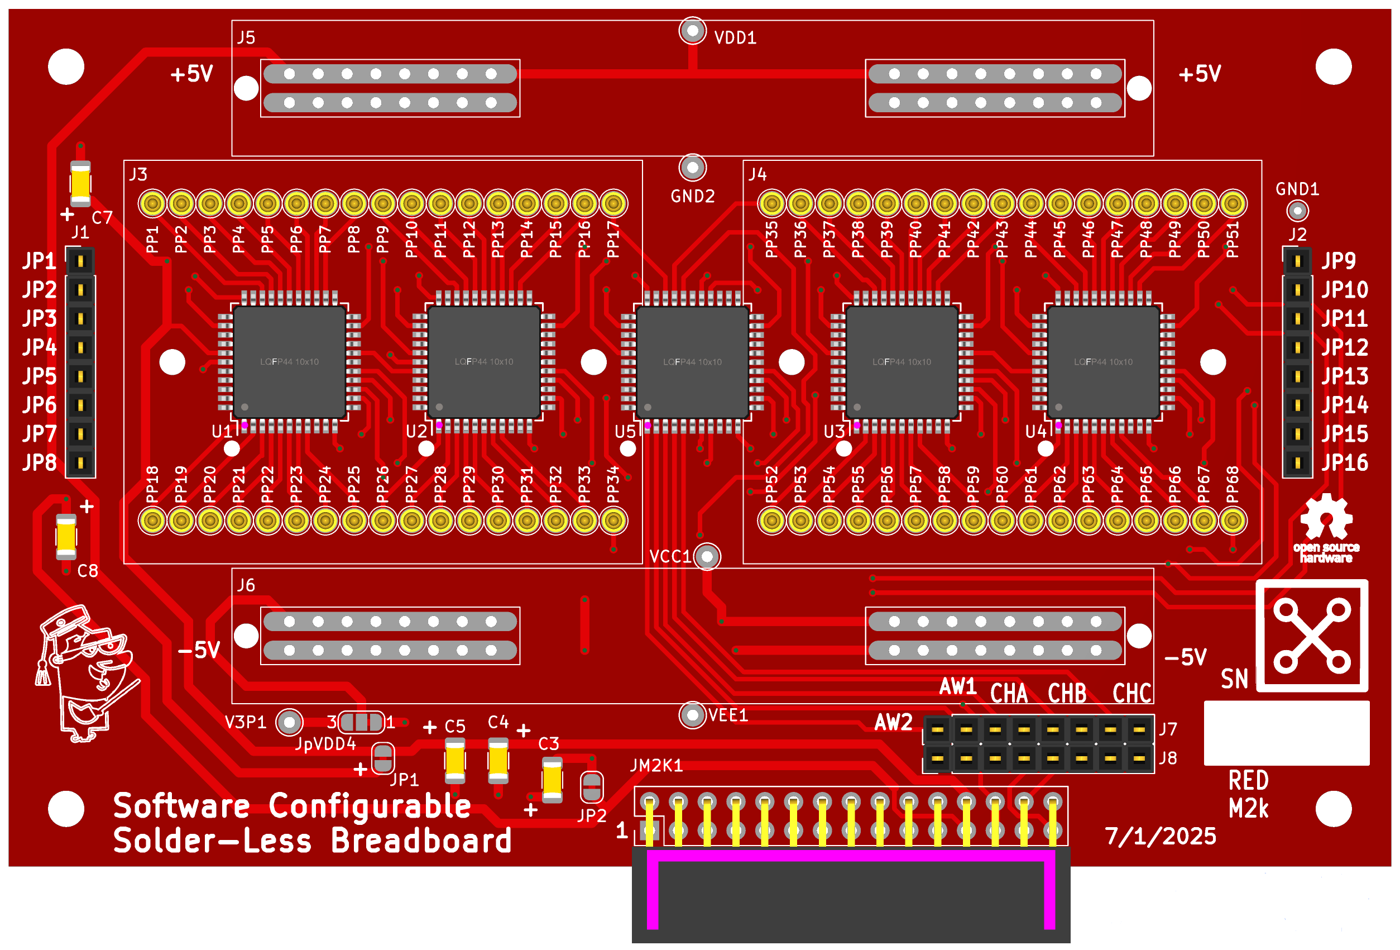
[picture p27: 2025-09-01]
PCB Projects/cross-point-exp-brd-mini-red2-m2k/M2k-cross-point-brd-v1.png

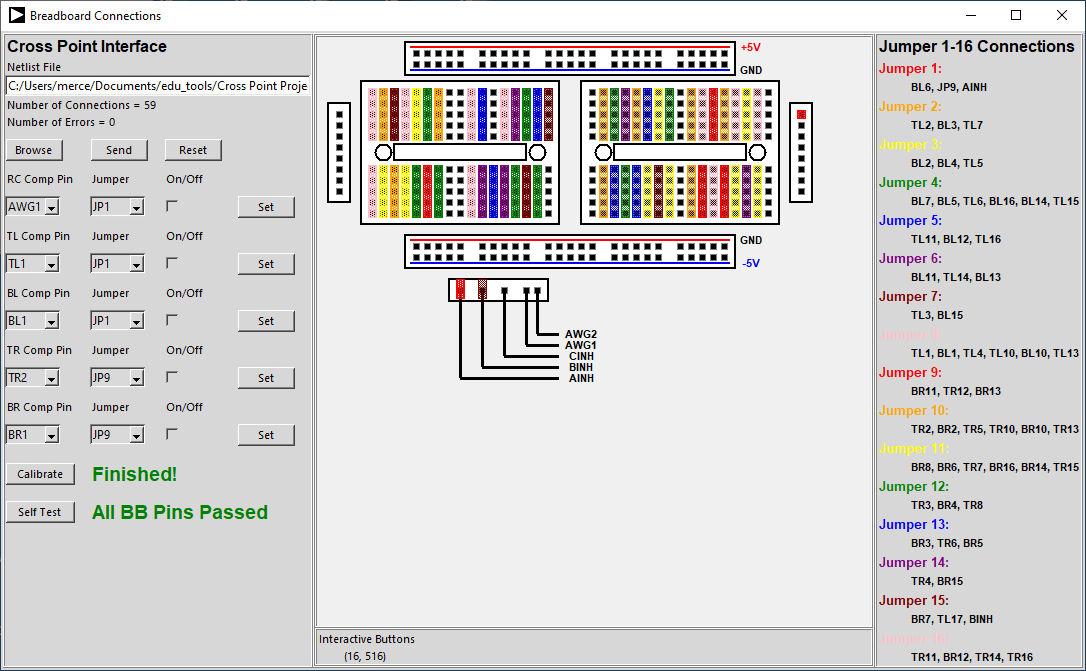
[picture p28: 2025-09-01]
Python UI/Crosspoint_RPI_UI_screen.png

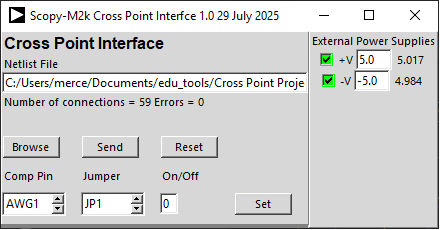
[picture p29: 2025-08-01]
Python UI/M2k/Scopy-M2k-Controls.png

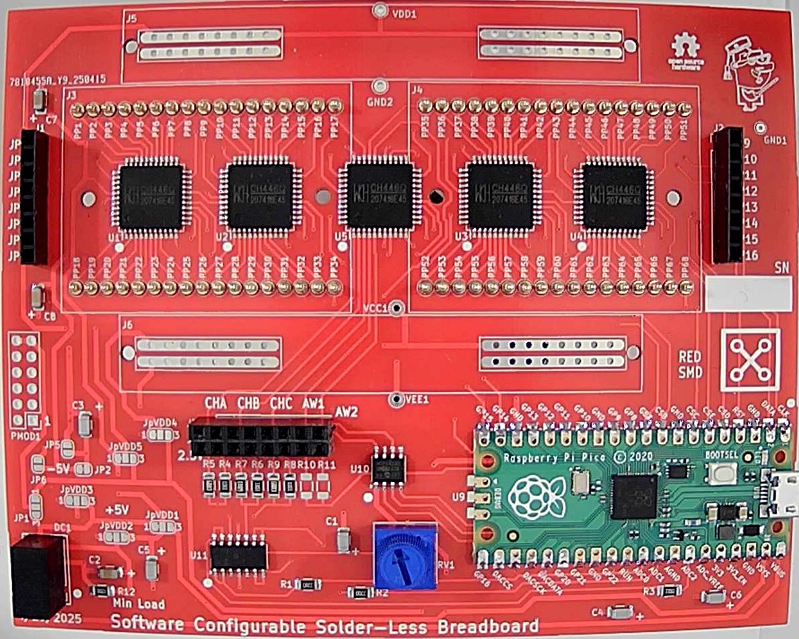
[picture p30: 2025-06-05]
PCB Projects/Red-JLCPCB-Assmb.jpg

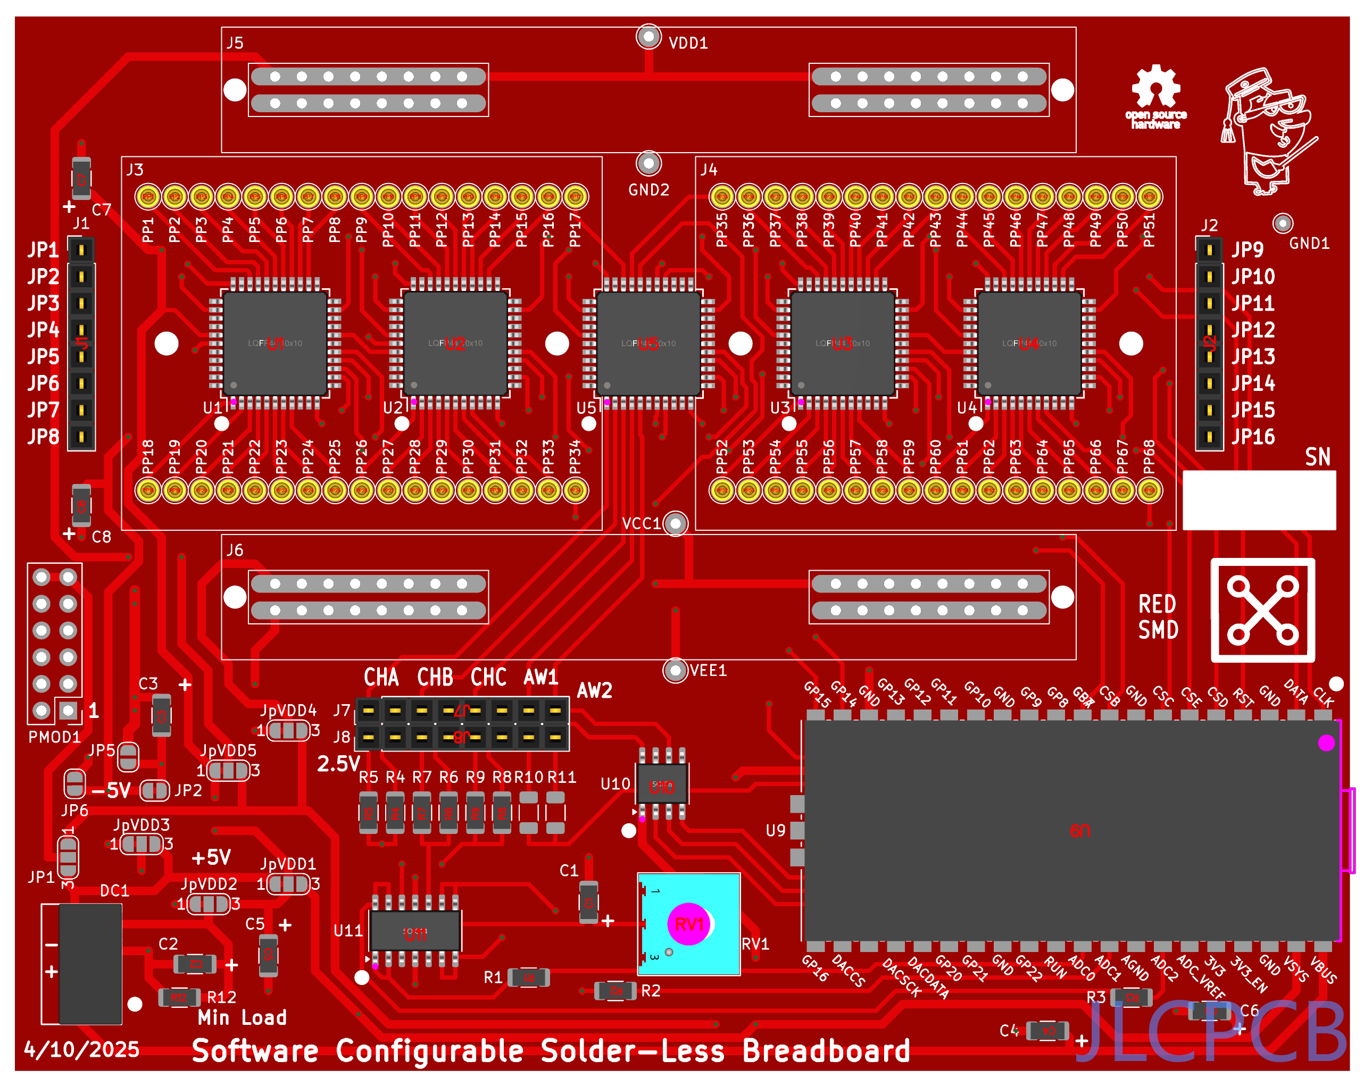
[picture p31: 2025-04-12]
PCB Projects/cross-point-exp-brd-mini-red2-sjmp/JLCPCB-red2-sjmp-top-placement.png

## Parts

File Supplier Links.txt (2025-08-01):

Narrow Fillister Head Slotted Screw
18-8 Stainless Steel, High-Profile, 2-56 Thread, 1/2" Long
https://www.mcmaster.com/91794a081/
Low-Strength Steel Hex Nut
Zinc-Plated, 2-56 Thread Size
https://www.mcmaster.com/90480A003/

2-56 UNC x 1/2 Inch Imperial Fillister Screws - Stainless Steel (A2)
Accu Product Code (APC): SFI-2-56-1/2-A2
https://accu-components.com/us/fillister-screws/71818-SFI-2-56-1-2-A2?google_shopping=1&c=2&gad_source=1&gad_campaignid=21073954785&gclid=Cj0KCQjwhO3DBhDkARIsANxrhTp4Be7q5WRHwLOS3neCBebzV_uRgCsj0xb-R9GfaVAqQOdO4SQEiDcaAlalEALw_wcB

Fillister Head Machine Screws Phillips Drive Full Coarse Thread #2-56 x 1/2 in Grade 18-8 Stainless Steel Plain
https://www.huyett.com/scrm6a-0002-0500188p

From DigiKey:
Solder paste 315-NC191LT10-ND:
https://www.digikey.com/en/products/detail/chip-quik-inc./NC191LT10/11480389?utm_adgroup=&gad_source=1
CF18JT330KCT-ND RES 330K OHM 5% 1/8W AXIAL X100 $1.68
CF18JT680KCT-ND RES 680K OHM 5% 1/8W AXIAL X100 $1.68
CF18JT220RCT-ND RES 220 OHM 5% 1/8W AXIAL  X100 $1.68
CF18JT470RCT-ND RES 470 OHM 5% 1/8W AXIAL  X100 $1.68
445-180818-1-ND CAP CER 0.47UF 25V X7R RADIAL X50
CRE1S0505SC DC DC CONVERTER 5V 1W 811-3196-ND $2.37 X 10 $23.70
RFM-0505S 5V isolated DC/DC converter
MCP4822 -E-P Dual Serial DAC X10
MCP6004 -E-P Quad OP-AMP X10
RPC8345-ND #2-56 nylon machine screws	
RPC7088-ND #2-56 nylon hex nuts

From Addicore:
10k Ohm White Knob Potentiometer
https://www.addicore.com/collections/variable-potentiometers/products/10k-ohm-white-knob-potentiometer

GS-050 50 tie point power strip
https://testequipmentusa.com/global-specialties-gs-050-bus-strip-50-tie-points-2-pack/

From Aliexpress:
RP-2040 Pi Pico boards
https://www.aliexpress.us/item/3256806917806174.html?
Color: RP2040 Type-C 4MB or Color: RP2040 Micro Type-C

1-10PCS SYB-170 Mini Solderless Prototype Breadboard
https://www.aliexpress.us/item/3256806379892335.html?

2-100Pcs CH446Q SMT LQFP-44 8x16 Matrix Analog Switch Array
https://www.aliexpress.us/item/3256806513688648.html?
https://www.wch-ic.com/products/CH446.html

5-500Pcs Pogo Pin Connector Pogopin Spring Loaded Through Hole 3mm
https://www.aliexpress.us/item/2255800849772402.html?
100Pcs Pogo Pin Connector Pogopin Spring Loaded Contact 3mm
https://www.aliexpress.us/item/3256807321702895.html?

1000Pcs SMD 3.5mm Pogo Pin Connector Pogopin Spring Loaded Model Number RIPZV
https://www.aliexpress.us/item/3256802604483723.html

100Pcs SMD 3.5mm Pogo Pin Connector Pogopin Spring Loaded Brand Name RTLECS
https://www.aliexpress.us/item/2255800849767469.html

200 Pcs SMD 3.5mm Pogo Pin Connector Pogopin Spring Loaded Model Number GC20-x Brand Name RTLECS
https://www.aliexpress.us/item/2255800580917781.html

Single row female header: 1X8
https://www.aliexpress.us/item/3256803241779203.html?
https://www.aliexpress.us/item/3256805226022984.html?

Dual row female header: 2X8
https://www.aliexpress.us/item/3256805948524386.html?
https://www.aliexpress.us/item/3256804148274564.html?

Dual row right angle female: 2X6
https://www.aliexpress.us/item/3256806810764627.html?
https://www.aliexpress.us/item/2255800144094493.html?

PCB fab and assembly:
 https://www.pcbway.com/
 https://jlcpcb.com/
 https://jlcpcb.com/parts
 macrofab.com (https://www.macrofab.com/)

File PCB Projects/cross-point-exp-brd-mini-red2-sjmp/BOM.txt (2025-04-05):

"Reference","Value","Datasheet","Footprint","Qty","DNP"
"C1,C2,C3,C4,C5,C6,C7,C8","0.22u","~","Capacitor_SMD:C_1808_4520Metric","8",""
"DC1","CME0505S3C","~","Connector_PinHeader_2.54mm:PinHeader_1x04_P2.54mm_Vertical","1",""
"GND1,GND2,TP6,VCC1,VDD1,VEE1","TestPoint","~","-- mixed values --","6",""
"J1,J2,J7,J8","Conn_01x08_Pin","~","Connector_PinHeader_2.54mm:PinHeader_1x08_P2.54mm_Vertical","4",""
"J3,J4","Solderless_mini_2Rows-17Pins","~","Library:Solderless_mini_mount_holes_2x17_P2.54mm","2",""
"J5,J6","Solderless_power-4Pins","~","Library:Solderless_power_2x4_P2.54mm","2",""
"JP1","SolderJumper_3_Open","~","Jumper:SolderJumper-3_P1.3mm_Open_RoundedPad1.0x1.5mm_NumberLabels","1",""
"JP3,JP4","SolderJumper_2_Open","~","Jumper:SolderJumper-2_P1.3mm_Open_RoundedPad1.0x1.5mm","2",""
"JpVDD1,JpVDD2,JpVDD3,JpVDD4,JpVDD5","Conn_01x03_Pin","~","Connector_PinHeader_2.54mm:PinHeader_1x03_P2.54mm_Vertical","5",""
"JVEE1","Conn_01x04_Pin","~","Connector_PinHeader_2.54mm:PinHeader_1x04_P2.54mm_Vertical","1",""
"PMOD1","Conn_02x06_Top_Bottom","~","Library:PMOD_Header_2x06_P2.54mm","1",""
"PP1,PP2,PP3,PP4,PP5,PP6,PP7,PP8,PP9,PP10,PP11,PP12,PP13,PP14,PP15,PP16,PP17,PP18,PP19,PP20,PP21,PP22,PP23,PP24,PP25,PP26,PP27,PP28,PP29,PP30,PP31,PP32,PP33,PP34,PP35,PP36,PP37,PP38,PP39,PP40,PP41,PP42,PP43,PP44,PP45,PP46,PP47,PP48,PP49,PP50,PP51,PP52,PP53,PP54,PP55,PP56,PP57,PP58,PP59,PP60,PP61,PP62,PP63,PP64,PP65,PP66,PP67,PP68","POGO_PIN_01X01_70-9150","","MF_Connectors:MF_Connectors-POGO_PIN_70-9150","68",""
"R1,R2,R3","220","~","Resistor_SMD:R_1206_3216Metric","3",""
"R4,R6,R8","330k","~","Resistor_SMD:R_1206_3216Metric","3",""
"R5,R7,R9","680k","~","Resistor_SMD:R_1206_3216Metric","3",""
"R10","33k","~","Resistor_SMD:R_1206_3216Metric","1",""
"R11","68k","~","Resistor_SMD:R_1206_3216Metric","1",""
"R12","510","~","Resistor_SMD:R_1206_3216Metric","1",""
"RV1","10k","~","Potentiometer_THT:Potentiometer_Bourns_3386P_Vertical","1",""
"U1,U2,U3,U4,U5","~","","JumperlessFootprints:LQFP44_Tight","5",""
"U9","Pico","","MCU_RaspberryPi_and_Boards:_SMD_TH","1",""
"U10","MCP4822","http://ww1.microchip.com/downloads/en/DeviceDoc/20002249B.pdf","Package_SO:SO-8_3.9x4.9mm_P1.27mm","1",""
"U11","MCP6004","http://ww1.microchip.com/downloads/en/DeviceDoc/21733j.pdf","Package_SO:SO-14_3.9x8.65mm_P1.27mm","1",""

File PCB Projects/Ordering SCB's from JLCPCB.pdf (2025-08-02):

## Step 1: Create an order

Navigate to JLCPCB (https://jlcpcb.com/?from=VGSU&gad_source=1&gad_campaignid=14179457750&gbraid=0AAAAABS1QqkVs0kspxxTUOpfzXbQFzQwS) and make a free account if you do not have one

Select “Order Now” in the top right of your screen


## Step 2: Upload Gerber

Click “Add Gerber File” in the middle of the screen

Navigate to your Cross Point Project (https://github.com/damercer/Cross-Point-Project) repository or clone it (https://www.notion.so/Making-Doug-s-Solderless-Breadboard-1a20f9dca44b80c89d19c69c578b6200?pvs=21) if you do not already have it, or alternatively follow the direct links in each step where a file is required

- Navigate to the zip file
Cross-Point-Project→PCB Projects→cross-point-exp-brd-mini-red2-sjmp →Gerbers→cross-point-exp-brd-mini-red2-sjmp.zip

OR

- Download zip directly
Follow this link (https://github.com/damercer/Cross-Point-Project/blob/main/PCB%20Projects/cross-point-exp-brd-mini-red2-sjmp/Gerbers/cross-point-exp-brd-mini-red2-sjmp.zip)
Press “view raw” to download

Select and upload the zip file

## Step 3: Select Build Specifications

The specifications are the defaults from JLCPBC with the following changes:

- PCB color RED
- PCB assembly ON
- PCBA type STANDARD
- Confirm Parts Placement YES (will have a pop up menu, check the box for “Do not confirm automatically”)

Price should be $9.40 at this point. Press “Next” below calculated price

Specification images:


## Step 4: Confirm Board Image

Top of Board | Bottom of Board


Confirm that your board matches with these images and select “NEXT”

## Step 5: Upload BOM and CPL files

NOTE: It is possible that the sheets contain extra, blank pages. If there are any delete them as the upload will fail if these files have multiple sheets

## BOM

Navigate to BOM:
Cross-Point-Project → PCB Projects → cross-point-exp-brd-mini-red2-sjmp → JLCPCB_BOM_RED2_SMD.xlsx

OR
Directly download BOM:
Follow this link (https://github.com/damercer/Cross-Point-Project/blob/main/PCB%20Projects/cross-point-exp-brd-mini-red2-sjmp/JLCPCB_BOM_RED2_SMD.xlsx) and press “view raw” to download

## CPL

Navigate to CPL:
Cross-Point-Project → PCB Projects → cross-point-exp-brd-mini-red2-sjmp → JLCPCB-red2-sjmp-top-pos.csv
OR

Directly download CPL:
Follow this link (https://github.com/damercer/Cross-Point-Project/blob/main/PCB%20Projects/cross-point-exp-brd-mini-red2-sjmp/JLCPCB-red2-sjmp-top-pos.csv) and press “download raw file

Click “Process BOM and CPL” which may take a few attempts to be accepted

## Step 6:Confirm BOM


Check values to be consistent with the design you are implementing, and select all checkboxes on the right side of the screen.

Note that by default Pogo pins will be deselected to ensure you notice the additional charge for their placement on the board (at .08/per pogo or 11.52/board)

Press “NEXT”

## Step 7: Confirm Board

Confirm that your board matches this image with components placed and press “NEXT”

## Step 9: Confirm Order

On the next screen you will see a bill for all materials and engineering for 5 boards, the total price in the top right should read $228.14, with a product weight of 1.47kg

Note that you can pay a surcharge for expedited assembly, which will increase price

To check out you must select a product description, this one seems like the most apt description, however I am unsure if this decision affects the order

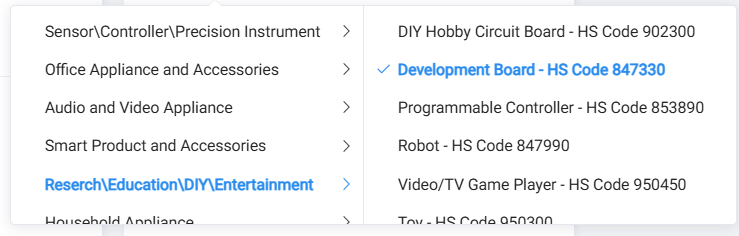
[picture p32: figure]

Select “Save to cart” and follow checkout instructions to place order

## Step 10: Final Assembly

Upon receiving boards from JLC, you will need to mount the breadboards to the pogo pins before use.

Per board, order four “Narrow Fillister Head Slotted Screw, 18-8 Stainless Steel, High-Profile, 2-56 Thread, 1/2" Long (https://www.mcmaster.com/91794a081/) and four Low-Strength Steel Hex Nut Zinc-Plated, 2-56 Thread Size (https://www.mcmaster.com/90480A003/) to attach two 170 Tie-Point Boards. (https://www.addicore.com/products/mini-breadboard-170-tie-points?variant=45759563006269) Lastly you will need two power rails per board: you may choose between 50 pins (https://www.notion.so/PPPC052LJBN-RC-Sullins-Connector-Solutions-Connectors-Interconnects-DigiKey-2000f9dca44b80bcb516ed6930df6d7f?pvs=21) and 60 pins, (https://testequipmentusa.com/global-specialties-gs-060-bus-strip-60-tie-points-2-pack/) both conveniently sold in packs of two, so buy one pack per board.

To attach, simply place each breadboard upon the pogo pins, thread the screws through the board holes, PCB holes, and the hex nut and tighten. The power rails can be stuck directly to the board by using the sticker on the back of the rails. A wire must lastly be soldered from the back of the board to the power rails, connecting to the underside of J5 and J6. It is recommended to test each column of the breadboard with a DMM in continuity mode.

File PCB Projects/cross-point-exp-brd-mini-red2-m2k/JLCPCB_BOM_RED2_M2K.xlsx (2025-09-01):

Comment | Designator | Footprint | JLCPCB Part#(optional)
10uF | C7, C8 | 1206 | C1849
470nF | C3,C4,C5 | 1206 | C6049896
CH446Q | U1,U2,U3,U4,U5 | LQFP-44(10x10) | C109471
2.54-2*15P Rt Angle Female | JM2K1 | 'Plugin,P=2.54mm | C2897435
2.54-1*8P Female or B-2200S08P-A120 | J1, J2, J7, J8 | Plugin,P=2.54mm | C124416
BWCD-L3.5W2.0H1.0 | PP1,PP2,PP3,PP4,PP5,PP6,PP7,PP8,PP9,PP10,PP11,PP12,PP13,PP14,PP15,PP16,PP17,PP18,PP19,PP20,PP21,PP22,PP23,PP24,PP25,PP26,PP27,PP28,PP29,PP30,PP31,PP32,PP33,PP34,PP35,PP36,PP37,PP38,PP39,PP40,PP41,PP42,PP43,PP44,PP45,PP46,PP47,PP48,PP49,PP50,PP51,PP52,PP53,PP54,PP55,PP56,PP57,PP58,PP59,PP60,PP61,PP62,PP63,PP64,PP65,PP66,PP67,PP68 | SMD Pogo Pin Spring Probe Connector | C2826547

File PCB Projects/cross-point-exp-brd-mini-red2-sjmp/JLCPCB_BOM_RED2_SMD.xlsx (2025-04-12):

Comment | Designator | Footprint | JLCPCB Part#(optional)
10uF | C2, C7, C8 | 1206 | C1849
470nF | C1,C3,C4,C5,C6 | 1206 | C6049896
330KΩ | R4, R6, R8 | 1206 | C17929
680KΩ | R5, R7, R9 | 1206 | C17974
220Ω | R1,R2,R3 | 1206 | C17957
RFM-0505S | DC1 | SIP,11.5x6mm | C22371855
470Ω | R12 | 1206_R | C4502
CH446Q | U1,U2,U3,U4,U5 | LQFP-44(10x10) | C109471
MCP4822-E/SN | U10 | SOIC-8 | C16040
MCP6004T-I/SL | U11 | SOIC-14 | C7378
Rapberry Pi Pico | U9 |  | C7203002
2.54-1*8P Female or B-2200S08P-A120 | J1, J2, J7, J8 | Plugin,P=2.54mm | C124416
3386P-1-103TLF | RV1 | Plugin-3P,9.5x9.5mm | C116302
BWCD-L3.5W2.0H1.0 | PP1,PP2,PP3,PP4,PP5,PP6,PP7,PP8,PP9,PP10,PP11,PP12,PP13,PP14,PP15,PP16,PP17,PP18,PP19,PP20,PP21,PP22,PP23,PP24,PP25,PP26,PP27,PP28,PP29,PP30,PP31,PP32,PP33,PP34,PP35,PP36,PP37,PP38,PP39,PP40,PP41,PP42,PP43,PP44,PP45,PP46,PP47,PP48,PP49,PP50,PP51,PP52,PP53,PP54,PP55,PP56,PP57,PP58,PP59,PP60,PP61,PP62,PP63,PP64,PP65,PP66,PP67,PP68 | SMD Pogo Pin Spring Probe Connector | C2826547

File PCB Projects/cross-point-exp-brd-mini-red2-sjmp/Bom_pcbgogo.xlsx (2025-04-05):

 | xxxx xxxx xxxxx xxPCS BOM (Sample Bill of Materials)
Quantity | Designator | Description | Value | Footprint | Manufacturer | Part Number | Buying Link as reference
1 | J7 | ZIF Connector, 0.5mm Dual Contact | XF2M-3515-1A | XF2M-3515-1A | Omron | XF2M-3515-1A
1 | U3 | IC NFC Initiator / HF Reader | AS3911B-AQFT | QFN32-5x5-tCR2 | Austria Micro Systems | AS3911B-AQFT
3 | C2, C70, C94 | Cap Ceramic C0G | 100pF | CAPC0402X60N | Various | 100pF 0402 50V 5% C0G
1 | J2 | Smart Card Connector Low profile | CCM01-2604 LFT T25 | CCM01-2604-LFT | C&K | CCM01-2604 LFT T25
2 | J5, J6 | Connector Coax MCRF-J | 73412-0110 | MCRF-J | Molex | 73412-0110
1 | J1 | Connector USB3.1 Type C | 632723300011 | 632723300011 | Wurth | 632723300011
7 | P3, P4, P5, P6, P7, P8, P9 | Header SIL Male THP, 2.54mm Pitch | SIL2P-2.54 | SIL2P-2.54 | Various | SIL2P-2.54
2 | L2, L3 | Inductor Chip for High Frequency Wire Wound | 160nH | LQW2BA | Murata | LQW2BANR16J00
4 | R1, R2, R3, R21 | Resistor Chip SMD | 330R | RESC0402X40N | Various | 330R 0402 1%
1 | R31 | Resistor Chip SMD | 100K | RESC0402X40N | Various | 100K 0402 1%

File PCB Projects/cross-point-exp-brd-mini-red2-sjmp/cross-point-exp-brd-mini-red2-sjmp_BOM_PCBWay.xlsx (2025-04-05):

 |  |  | cross-point-exp-brd-mini-red2-smd-PCS BOM (Bill of Materials)
Item # | *Designator | *Qty | Manufacturer | *Mfg Part # | Description / Value | *Package/Footprint | Type | Your Instructions / Notes
1 | U9 | 1 | TZT | RP2040 TYPE-C | RPi_Pico RP2040 Micro Type-C |  | SMD
2 | U10 | 1 | Microchip | MCP4822 | Serial DUAL DAC -40-85 C 8-SOIC | 8-SOIC | SMD
3 | U11 | 1 | Microchip | MCP6004 | IC OPAMP Quad -40-85 C 14-SOIC | 14-SOIC | SMD
4 | DC1 | 1 | RFM | RFM-0505S | Isolated 5V DC-DC converter | 4 pin SIP | thru-hole
5 | U1,U2,U3,U4,U5 | 5 | WinChipHead (WCH) | CH446Q | 8x16 analog switch array chip CH446Q | LQFP44 | SMD
6 | R1,R2,R3 | 3 | Panasonic |  | RES 220 OHM 1/8W 1206 SMD | 1206 | SMD
7 | R4,R6,R8 | 3 | Panasonic |  | RES 330k OHM 1/8W 1206 SMD | 1206 | SMD
8 | R5,R7,R9 | 3 | Panasonic |  | RES 680k OHM 1/8W 1206 SMD | 1206 | SMD
9 | R12 | 1 |  |  | RES 470 OHM 1/8W 1206 SMD | 1206 | SMD
10 | C1,C3,C4,C5,C6 | 5 | Murata |  | CAP CER 0.47UF 16V X7R 1808 | 1808 | SMD
11 | C2,C7,C8 | 3 | Murata |  | CAP CER 4.7UF 16V X7R 1808 | 1808 | SMD
12 | RV1 | 1 |  |  | 10k Ohm White Knob Potentiometer |  | thru-hole
13 | J1,J2,J7,J8 | 4 |  |  | Connectors VERTICAL 1X8 Female | 8P Thru Hole | thru-hole
14 | JpVDD1,JpVDD2,JpVDD3,JpVDD4,JpVDD5 | 4 |  |  | Connectors VERTICAL 1X3 Male |  | thru-hole
15 | JVEE1 | 1 |  |  | Connectors VERTICAL 1X4 Male |  | thru-hole
16 | PP1,PP2,PP3,PP4,PP5,PP6,PP7,PP8,PP9,PP10,PP11,PP12,PP13,PP14,PP15,PP16,PP17,PP18,PP19,PP20,PP21,PP22,PP23,PP24,PP25,PP26,PP27,PP28,PP29,PP30,PP31,PP32,PP33,PP34,PP35,PP36,PP37,PP38,PP39,PP40,PP41,PP42,PP43,PP44,PP45,PP46,PP47,PP48,PP49,PP50,PP51,PP52,PP53,PP54,PP55,PP56,PP57,PP58,PP59,PP60,PP61,PP62,PP63,PP64,PP65,PP66,PP67,PP68 | 68 | BAT WIRELESS | BWCD-L3.5W2.0H1.0 | 3.5mm Pogo Pin Connector Pogopin Spring Loaded | 1P | SMD
Need a quick and accurante quote? Need an efficient production? Please read SMT Ordering Necessary Files & Info in 1 minute. Thank you very much! (https://www.pcbway.com/smt_ordering_guide.html)
Click for Instructions on How to Create a BOM (https://www.pcbway.com/blog/PCB_Assembly/How_to_Build_a_BOM__Bill_Of_Materials_.html)

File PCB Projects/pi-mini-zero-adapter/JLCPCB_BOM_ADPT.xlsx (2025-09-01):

Comment | Designator | Footprint | JLCPCB Part#(optional)
10uF | C1,C2,C3 | 1206 | C1849
330KΩ | R6,R8,R10,R12 | 1206 | C17929
680KΩ | R5,R7,R9,R11 | 1206 | C17974
3.9k | R14,R15 | 1206 | C17883
33k | R16,R17 | 1206 | C18004
24k | R18,R19 | 1206 | C17960
20k | R20,R21 | 1206 | C18003
120Ω | R22 | 1206 | C17909
390Ω | R1,R2,R3,R4,R13,R23 | 1206 | C4491
MC33202DR2G | U4 | SOIC-8 | C43122
MCP4822-E/SN | U3 | SOIC-8 | C16040
MCP6004T-I/SL | U2 | SOIC-14 | C7378

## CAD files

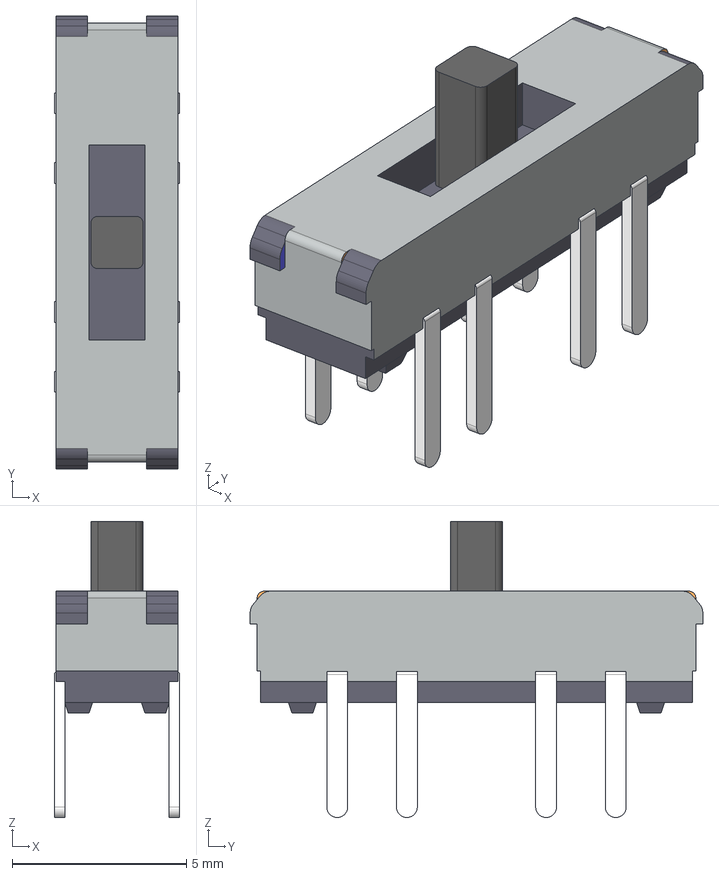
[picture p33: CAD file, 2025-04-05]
PCB Projects/cross-point-exp-brd-mini-red2-m2k/Symbols and Footprints/3dmodels/SSSS223600.step
3.60 x 13.0 x 8.50 mm

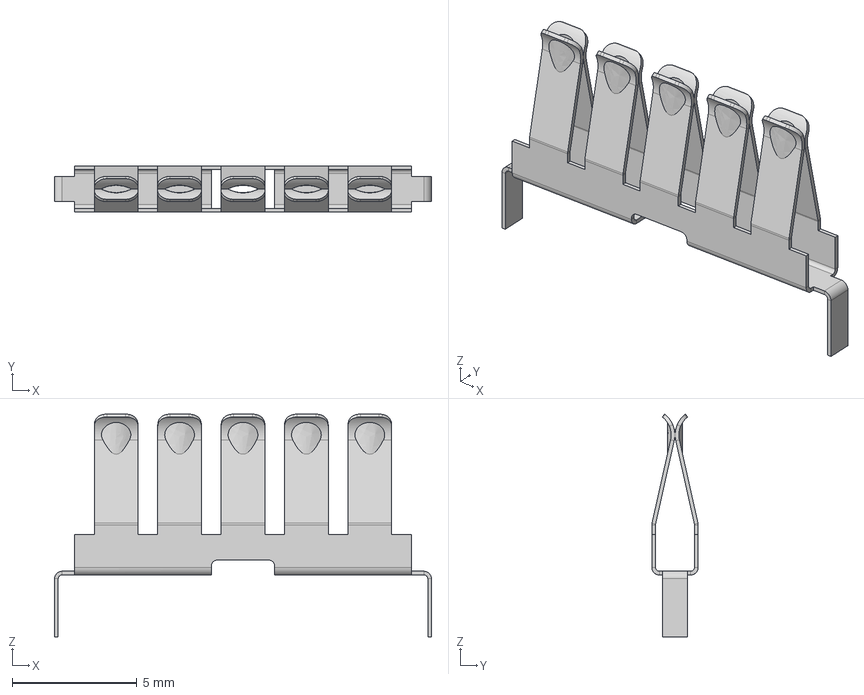
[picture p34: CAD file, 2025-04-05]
PCB Projects/cross-point-exp-brd-mini-red2-m2k/Symbols and Footprints/3dmodels/bbSimple v8.step
15.1 x 1.86 x 8.92 mm

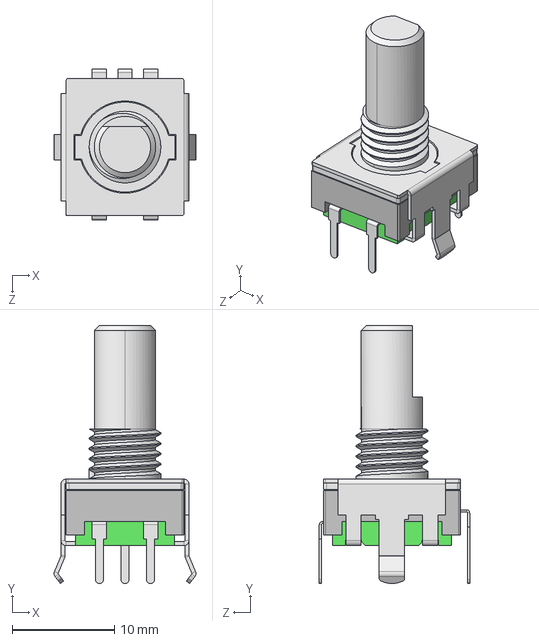
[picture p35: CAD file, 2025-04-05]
PCB Projects/cross-point-exp-brd-mini-red2-m2k/Symbols and Footprints/3dmodels/PEC11R-4215F-S0024--3DModel-STEP-56544.STEP
13.9 x 25.2 x 14.7 mm

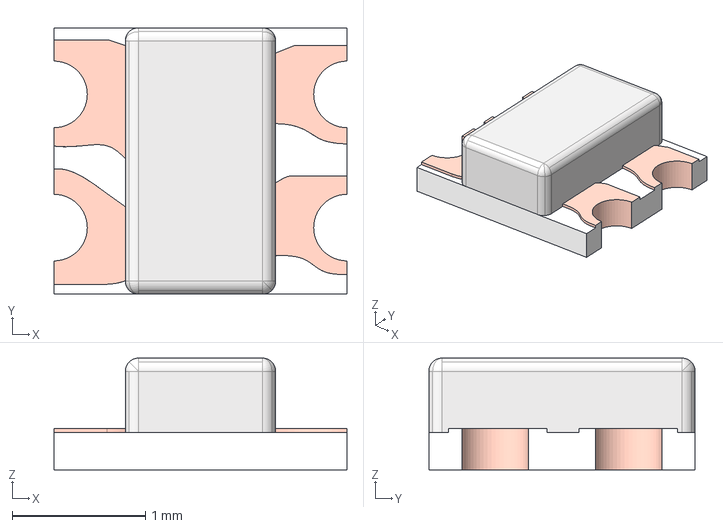
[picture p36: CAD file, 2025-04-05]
PCB Projects/cross-point-exp-brd-mini-red2-m2k/Symbols and Footprints/3dmodels/WS2812C-2020_Color.step
2.20 x 2.00 x 0.84 mm
ws2812c-2020 v2.step
ws2812c-2020 v2

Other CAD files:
PCB Projects/cross-point-exp-brd-mini-red2-m2k/Symbols and Footprints/3dmodels/bbSimple v1.step

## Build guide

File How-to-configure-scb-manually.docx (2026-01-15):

# How to manually wire a circuit using the Software Configurable Breadboard

Summary: This Proof of Skills assignment walks the reader through the best practices for using the manual configuration controls in the SCB User Interface. As the name implies the SCB is configured or programed as it were from a list of component locations and connections, often from a text file which can be thought of as the “program” to set up the board.

Step1:

Looking at the schematic of the circuit to be wired:

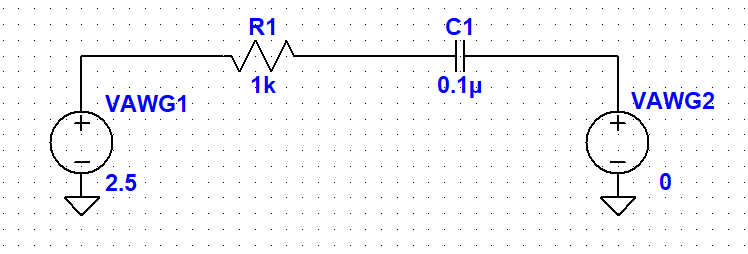
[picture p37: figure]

First Node

Second Node

Third Node

This simple example consists of a resistor and a capacitor connected in series. As can be seen in this example the circuit has just three nodes, the end of the series resistor R1, the end of the series capacitor C1 and the node in the middle. In the schematic we also need to consider special connections to nodes that represent the SCB waveform generator outputs (VAWG1, VAWG2) and scope inputs (AINH, BINH, CINH) to view waveforms.

To program the SCB hardware we need to decide where on the breadboard to insert or place the components R1 and C1. Between the 34 possible locations on each of the left and right side breadboard there are many ( > 100 ) possible ways to place R1 and C1. To keep things relative simple it is generally good practice for two terminal components like R1 and C1 to use breadboard holes on either side of the center gutter of the breadboard which divides the top and bottom sections.

In the SCB interface the following naming scheme is used for the breadboard holes. First we distinguish between the left and right side by using L and R in the names. Next we distinguish between the top and bottom sections by using T and B in the names. Finally the holes in each section are numbered from 1 to 17 left to right. Thus the left most location in the top section of the left breadboard is named TL1. The location just below that one on the opposite side of the central gutter in the bottom section will be named BL1. All the other locations on the breadboard(s) are named similarly.

With this in mind a good choice would be to place R1 between the TL2 and BL2 holes and place C2 between the TL4 and BL4 holes.

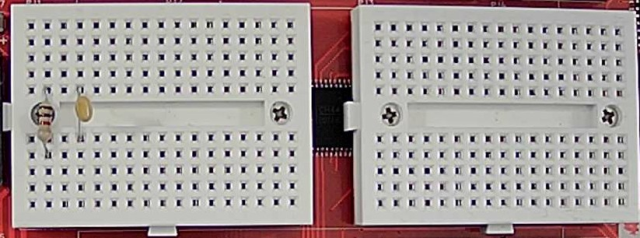
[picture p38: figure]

Step 2:

With the SCB connected to the computer over USB, Launch the Alice-universal-alpha.pyw python program. At this point the main Oscilloscope window and the AWG controls window can be minimized while configuring the SCB.

The controls to manually configure the SCB appear along the left side of the Cross Point Interface window (it might say either RED2 or RED3 depending on the hardware version of the SCB you have). In the center of the window is a graphical depiction of the breadboard. This is used to display how the various jumpers (JP1-16) are connected to the 67 possible breadboard locations. On the left side is an inventory of how the jumper resources are being used. That is generally not something you need to pay much attention to unless you have a very large circuit.

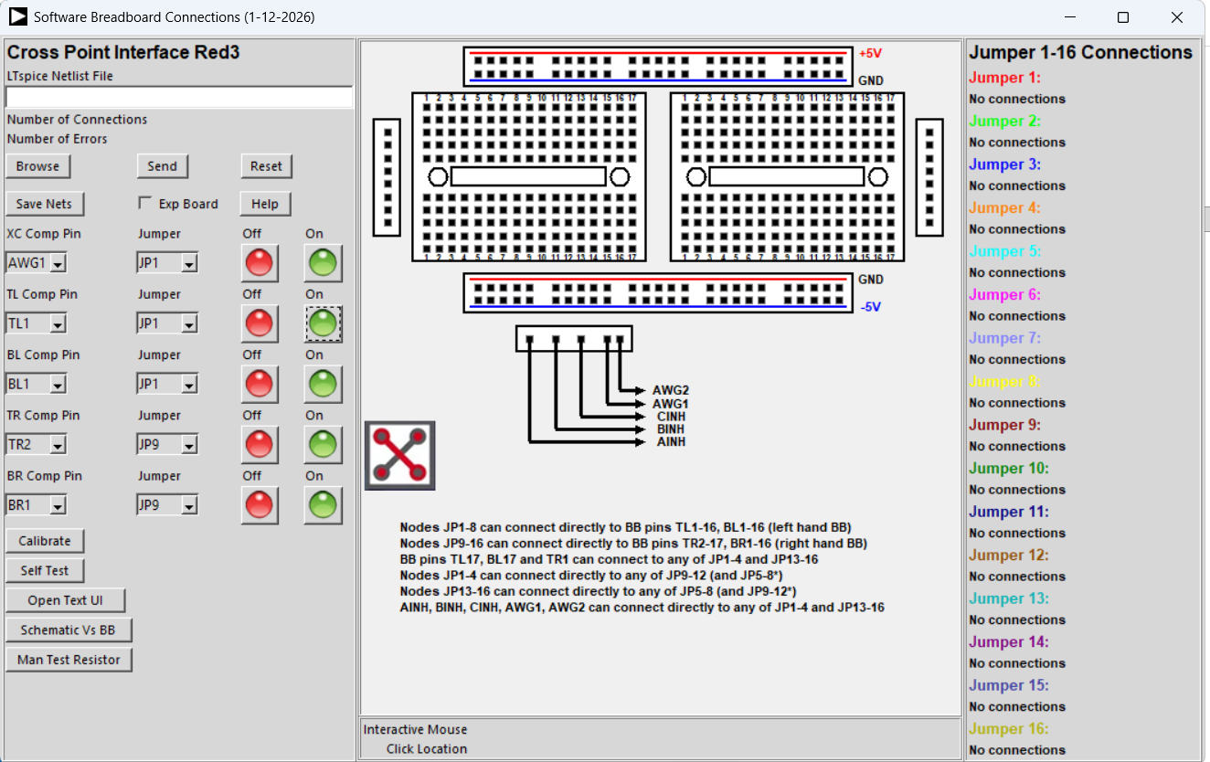
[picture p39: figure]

Click on the Open Text UI by clicking on the button on the right hand side of the Cross Point Interface window.

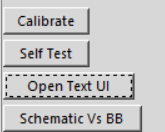
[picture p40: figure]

This will open the empty blank text editor / message display window.

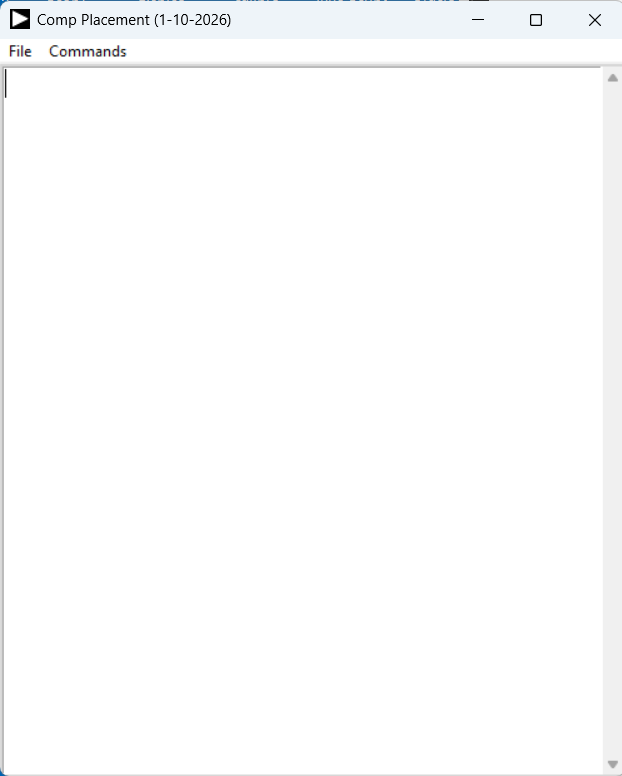
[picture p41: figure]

You now have to decide which of the 8 possible “jumpers” associated with the left side breadboard to assign to the three nodes in your circuit. The simplest approach is to simply start with JP1 for the end of R1, JP2 for the middle junction of R1 and C1 and JP3 for the end of C1.

JP1

JP2

JP3

To connect jumper JP1 to the top of resistor R1 there are two ways of doing this (more on the second way in Step 3). The first way is to select TL2 and JP1 using the TL set of the manual controls on the left side and clicking on the green On button to turn on the connection between TL2 and JP1:

The TL2 location on the breadboard will now be colored with the color associated with JP1.

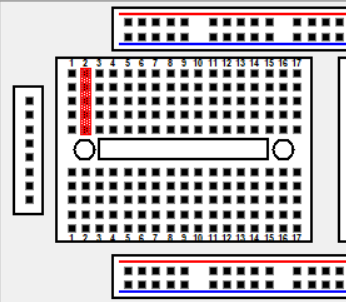
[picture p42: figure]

You will also notice that, with the Text Editor screen open, a line of text is added that lists this connection.

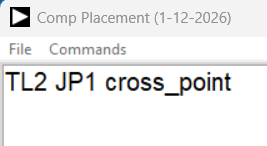
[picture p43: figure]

Similarly, to connect the other end of resistor R1 to JP2 select the BL2 and JP2 using the BL set of the manual controls on the left side and clicking on the green On button to turn on the connection between BL2 and JP2:

The BL2 location on the breadboard will now be colored with the color associated with JP2 and a second line of text is added in the Text Editor.

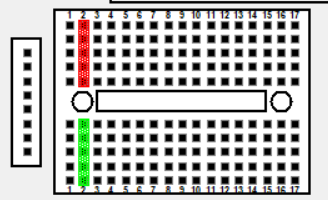
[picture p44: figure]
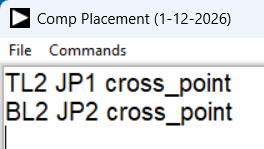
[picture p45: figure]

Do the same procedure for connecting C1 at TL4 and BL4 to JP2 and JP3. The results should look like this:

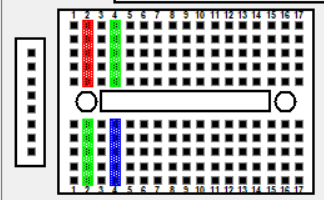
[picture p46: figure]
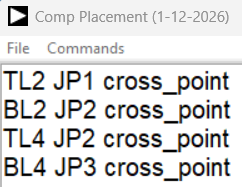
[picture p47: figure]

At this point we need to connect the two AWG outputs and the three Scope inputs to the circuit. These 5 connections are done using the XC Comp Pin control:

Select AWG1 and JP1, AWG2 and JP3, AINH and JP1, BINH and JP2, CINH and JP3 clicking on the green On button for each combination.

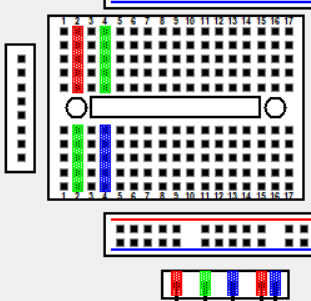
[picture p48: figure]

The Text Editor should now look like this with one line for each connection that is made:

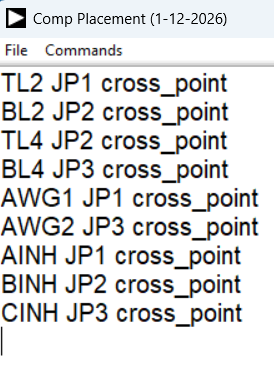
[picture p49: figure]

If you make any errors along the way simple remove the offending line from the Editor and redo the manual connection.

Step 3:

The second and perhaps faster way to program the connections once you get more familiar with using the SCB is to just type in the required connections to the Text Editor. Since you have already filled in most of the connections in Step 2, you can save this list to a file by clicking Save As in the Files drop down menu:

Enter the name you wish to save the file as.

There are two additions to the connections list that are needed to completely describe your circuit and that is the placement of R1 at TL2, BL2 and C1 at TL4, BL4. This is done by typing in the following two lines in the Editor:

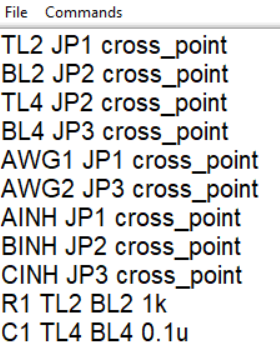
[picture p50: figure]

Again be sure to Save these additions to disk before moving to the final Step. The text file can be opened and edited to change any of the connections manually as needed.

Step 4:

Click on the Commands dropdown menu and select the Send From Editor command.

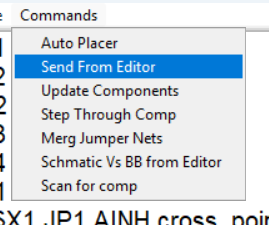
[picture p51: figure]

The SCB is Reset and the connections are now configured from this list of connections. The text screen will now be blanked (that is why we reminded you to save your work before doing this step) and the R1 and C1 locations will be displayed. To add back the Jumper connections click on the Merg Jumper Nets command.

To display where R1 and C1 have been placed on the breadboard graphic select the Update Components command.

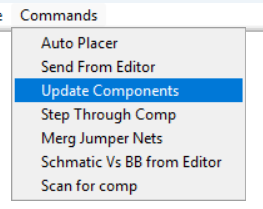
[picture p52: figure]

Resistor and Capacitor symbols will now be added to the breadboard display indicating where to insert R1 and C1.

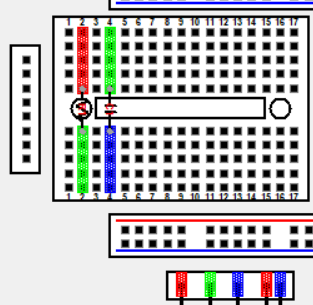
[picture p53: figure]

Text showing the location of R1 and C1 will also appear in the Text Editor window.

You can also step through the list of components one at a time by selecting the Step Through Comp command rather than Update Components.

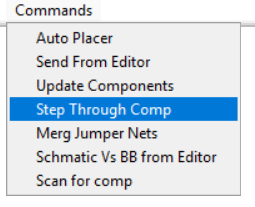
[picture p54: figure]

The SCB is now configured and you can procced with setting up the AWG and Scope channels to measure your circuit.

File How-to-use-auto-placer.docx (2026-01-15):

# How to use Auto Placer in Software Configurable Breadboard

Summary: This Proof of Skills assignment walks the reader through the best practices for using the Auto Placer function in the SCB User Interface. As the name implies the SCB is configured or programed as it were from a net list file which can be thought of as the “program” to be run.

Step1:

Open the simple-example-autoplace.asc schematic in LTspice. Or enter it as an new schematic from the picture below.

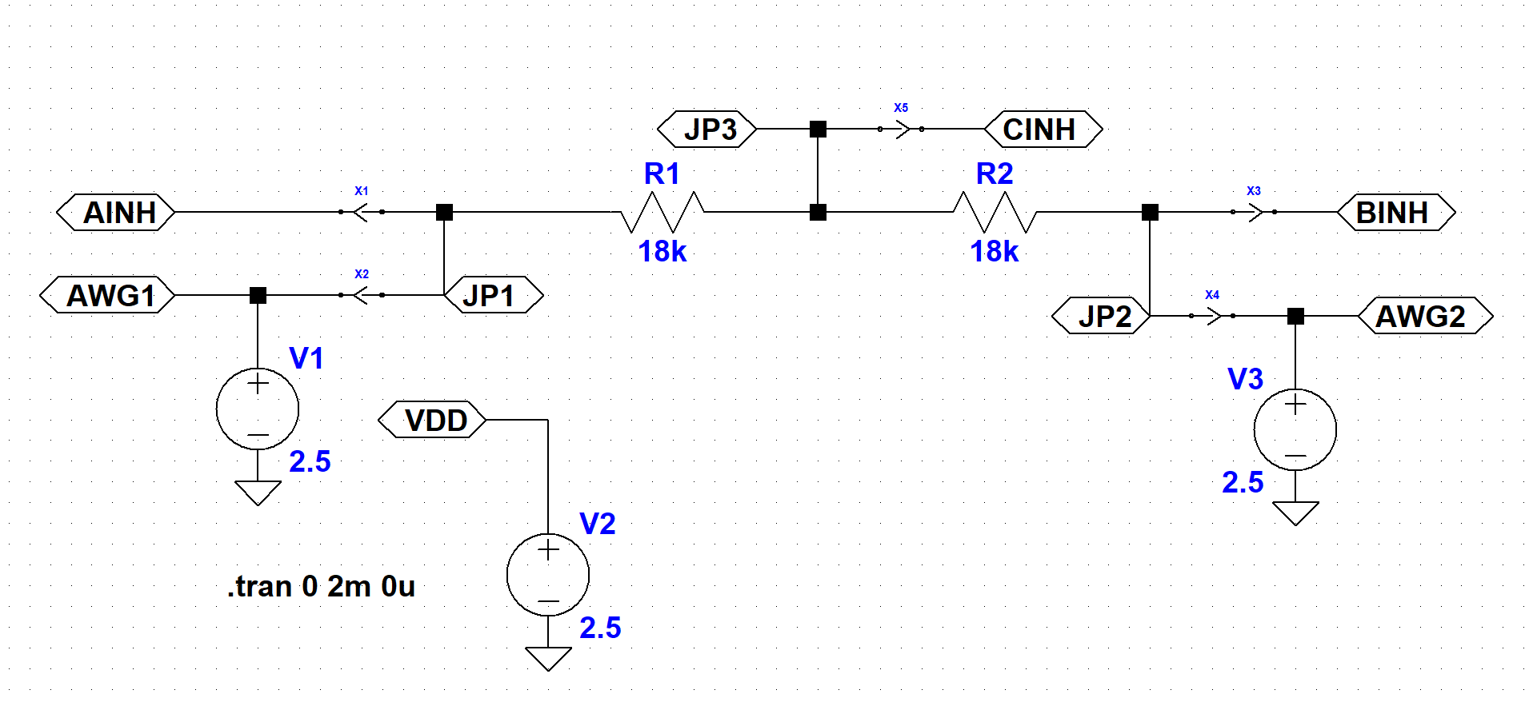
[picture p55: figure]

This simple example consists of two resistors connected in series. As can be seen in this example the circuit has just three nodes, the two ends of the series resistors (with net labels JP1 and JP2) and the middle node (with net label JP3). In the schematic we also join or connect 5 special nodes that represent the SCB waveform generator outputs (AWG1, AWG2) and scope inputs (AINH, BINH, CINH) to the circuit nodes. This is done by placing cross_point symbols between these nodes and one of the JP nodes. You can’t add two different net labels to the same node in LTspice. Note that the pointed side of the cross_point symbol points away from the JP nodes. Also note that there is no placement information with regard to R1 and R2 in the form of additional cross_point symbols in the schematic at this point.

To program the SCB hardware we need to save the Spice net list to a .cir file by clicking on the View drop down menu and selecting the Update and View SPICE netlist.

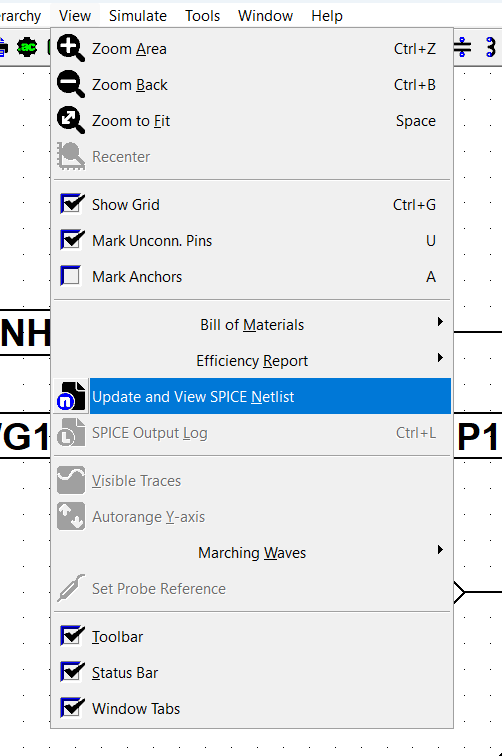
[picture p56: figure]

A text window will open showing the net list file to be saved.

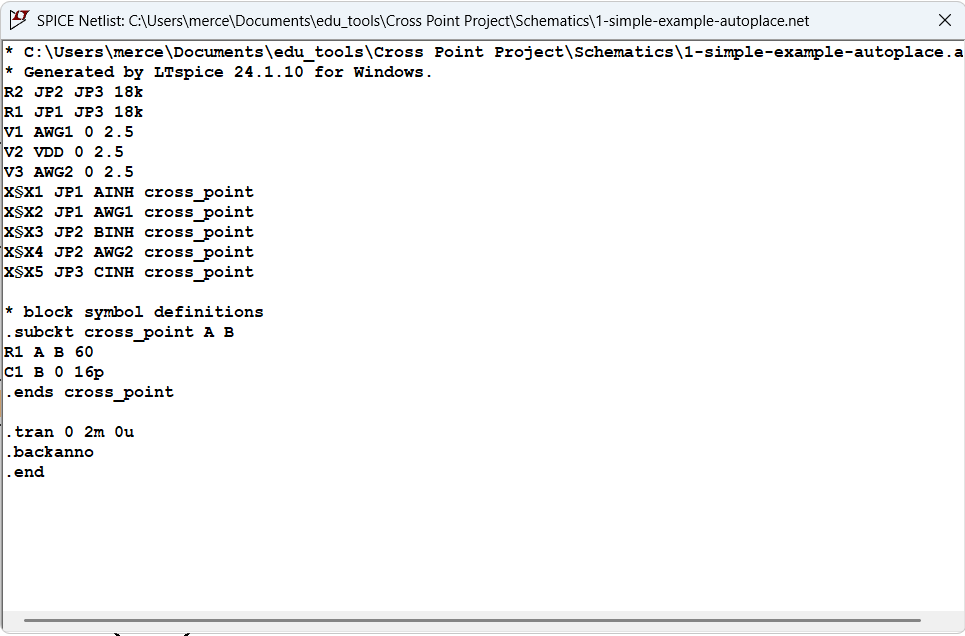
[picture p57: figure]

Right click in the text window and this dialog box will appear. Click on Edit as Independent Netlist to save file to disk.

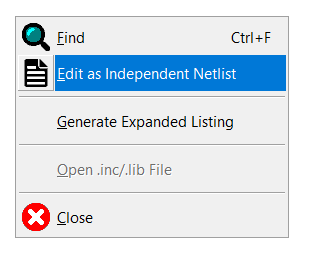
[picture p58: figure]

Step 2:

You now have a net list file to use to configure the SCB using the Auto Placer.

With the SCB connected to the computer over USB, Launch the Alice-universal-alpha.pyw python program. At this point the main Oscilloscope window and the AWG controls window can be minimized while configuring the SCB.

Click on the Open Text UI by clicking on the button on the right hand side of the Cross Point Interface window.


This will open the empty blank text editor / message display window.


Click on the Commands dropdown menu and select the Auto Placer command.

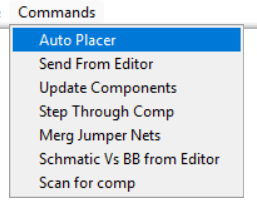
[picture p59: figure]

A file selector will open because you have not yet entered a file name.

Select and open the simple-example-autoplace.cir file you generated in Step 1.

The Auto Placer will now run placing the two resistors in this simple example netlist. A new expanded net list will appear in the text editor. Note that at this point this version of the net list can be saved to disk using the Save As File command.

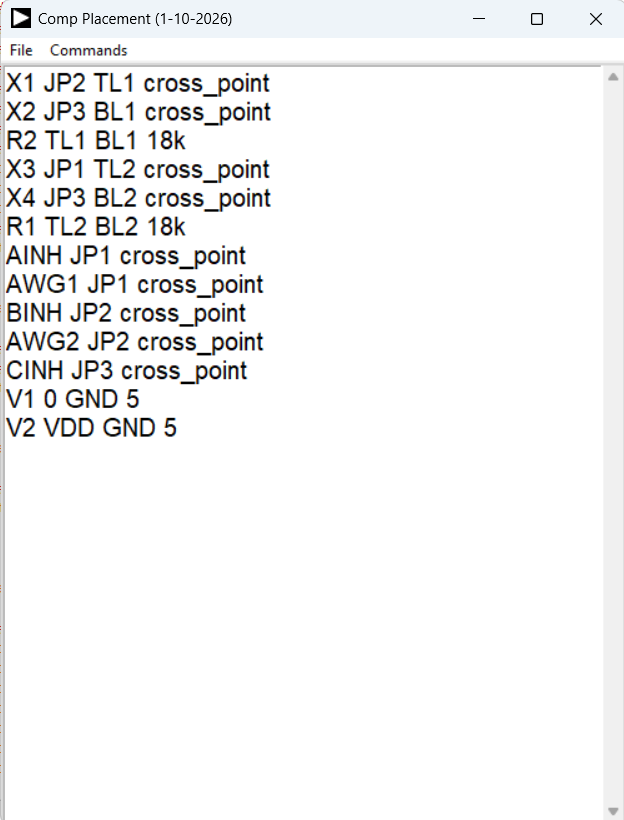
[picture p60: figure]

This new netlist has placed resistor R1 between the TL2 and BL2 breadboard holes and resistor R2 between the TL1 and BL1 breadboard holes. It chose the left side breadboard because jumpers in the range JP1-8 were called out in the schematic. If jumpers in the range of JP9-16 were used then it would have placed the components in the right side breadboard. (The order that the components are placed is based on the order they appear in the netlist and not based on the components name)

Now you need to configure the SCB connections from this new expanded net list by selecting the Send from Editor command from the drop down menu.


The text screen will now be blanked and the new SCB connections will be displayed.

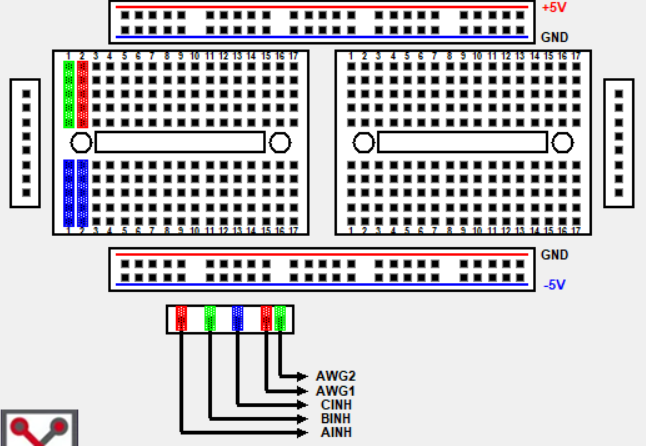
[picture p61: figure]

To display where R1 and R2 have been placed select the Update Components command.


Resistor symbols will now be added to the breadboard display indicating where to insert R1 and R2.

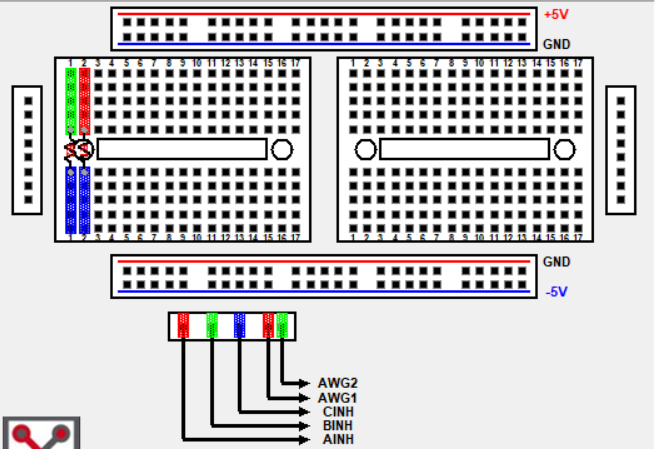
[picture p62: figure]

Text showing the location of R1 and R2 will also appear in the Text Editor window.

You can also step through the list of components one at a time by selecting the Step Through Comp command rather than Update Components.


The SCB is now configured and you can procced with setting up the AWG and Scope channels to measure your circuit.

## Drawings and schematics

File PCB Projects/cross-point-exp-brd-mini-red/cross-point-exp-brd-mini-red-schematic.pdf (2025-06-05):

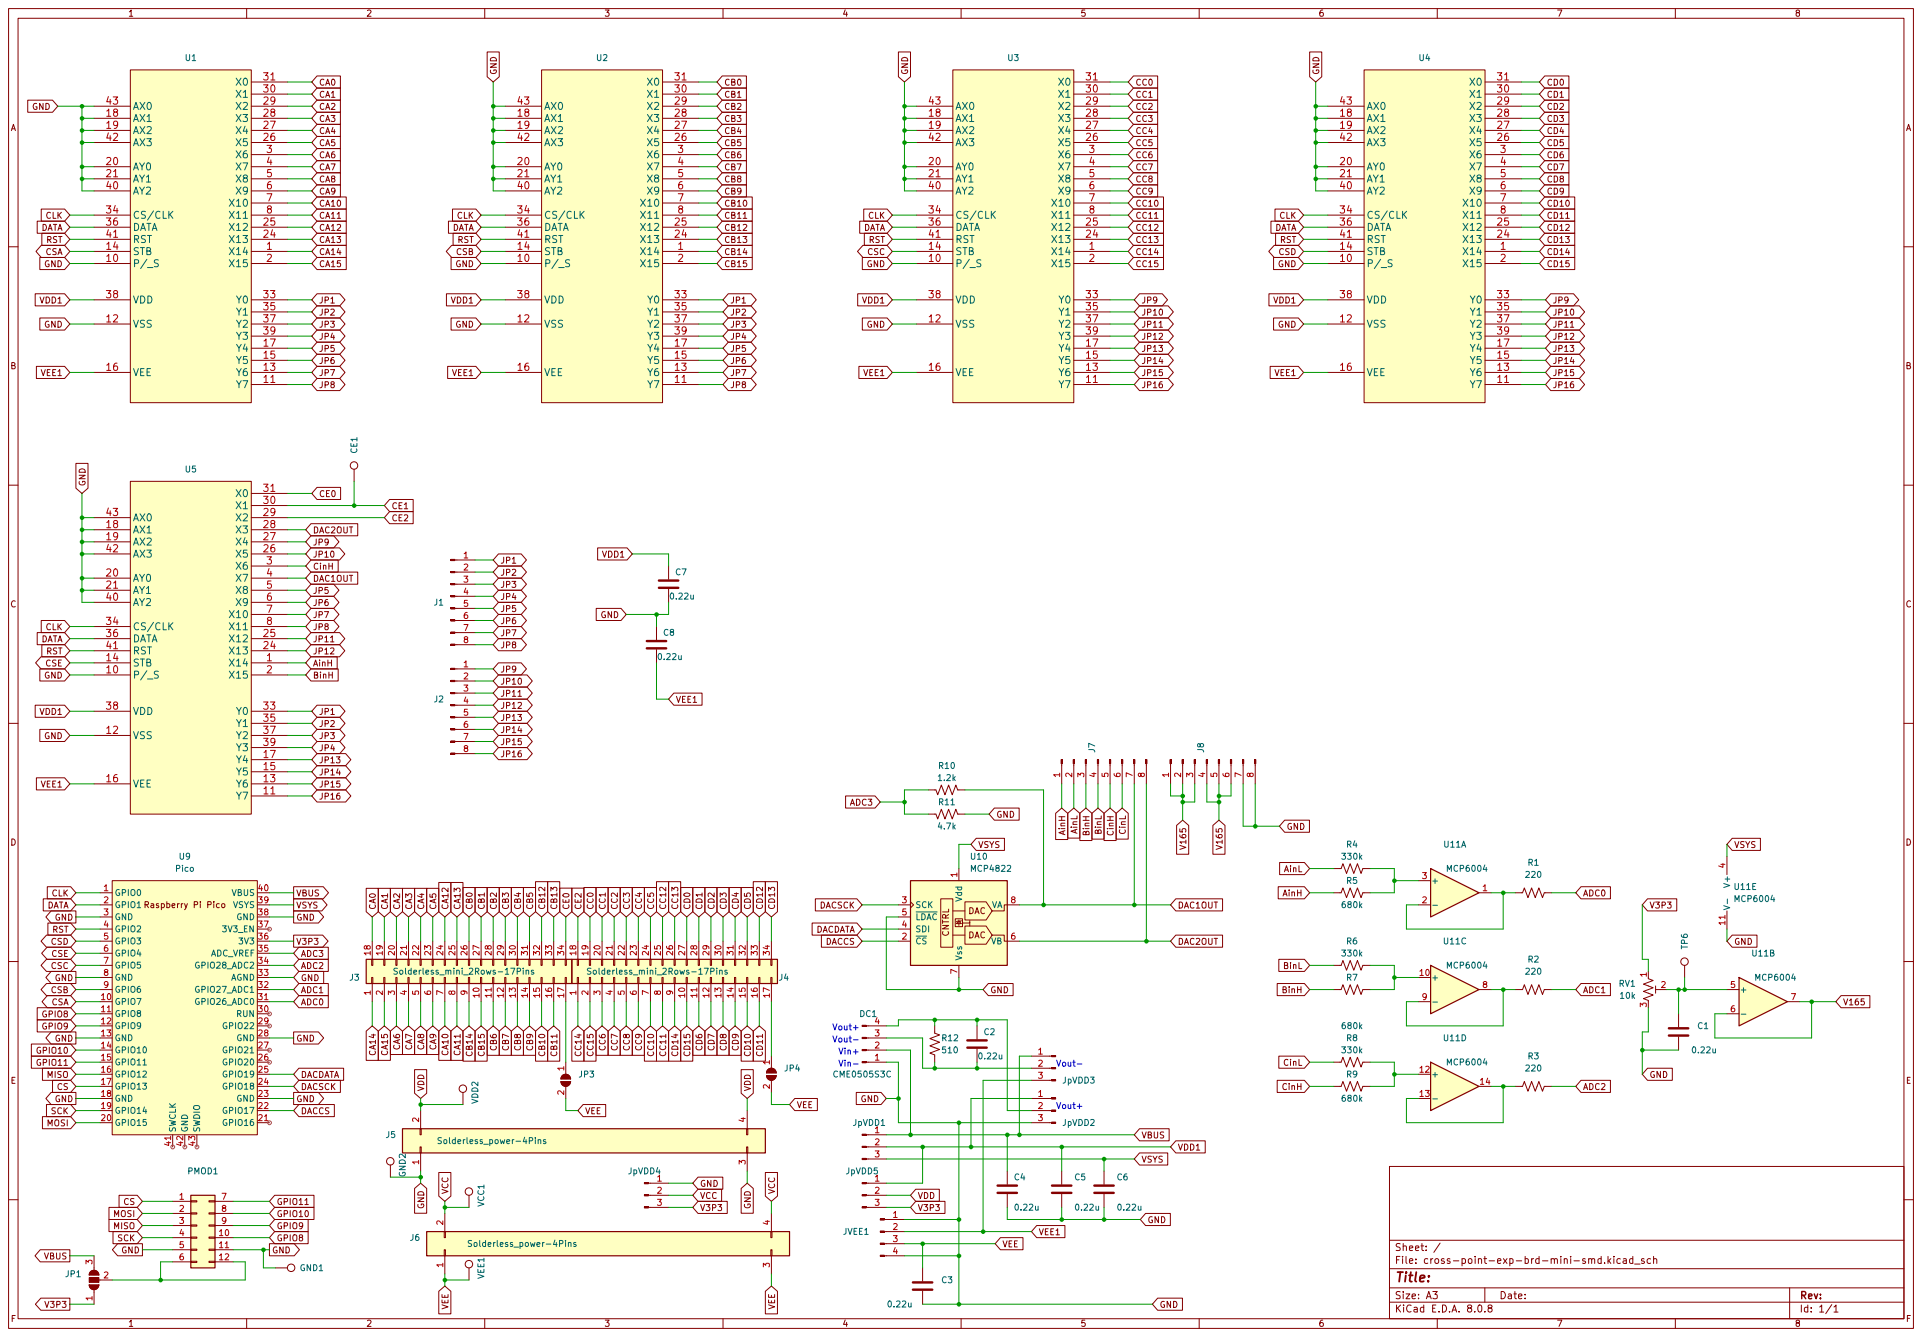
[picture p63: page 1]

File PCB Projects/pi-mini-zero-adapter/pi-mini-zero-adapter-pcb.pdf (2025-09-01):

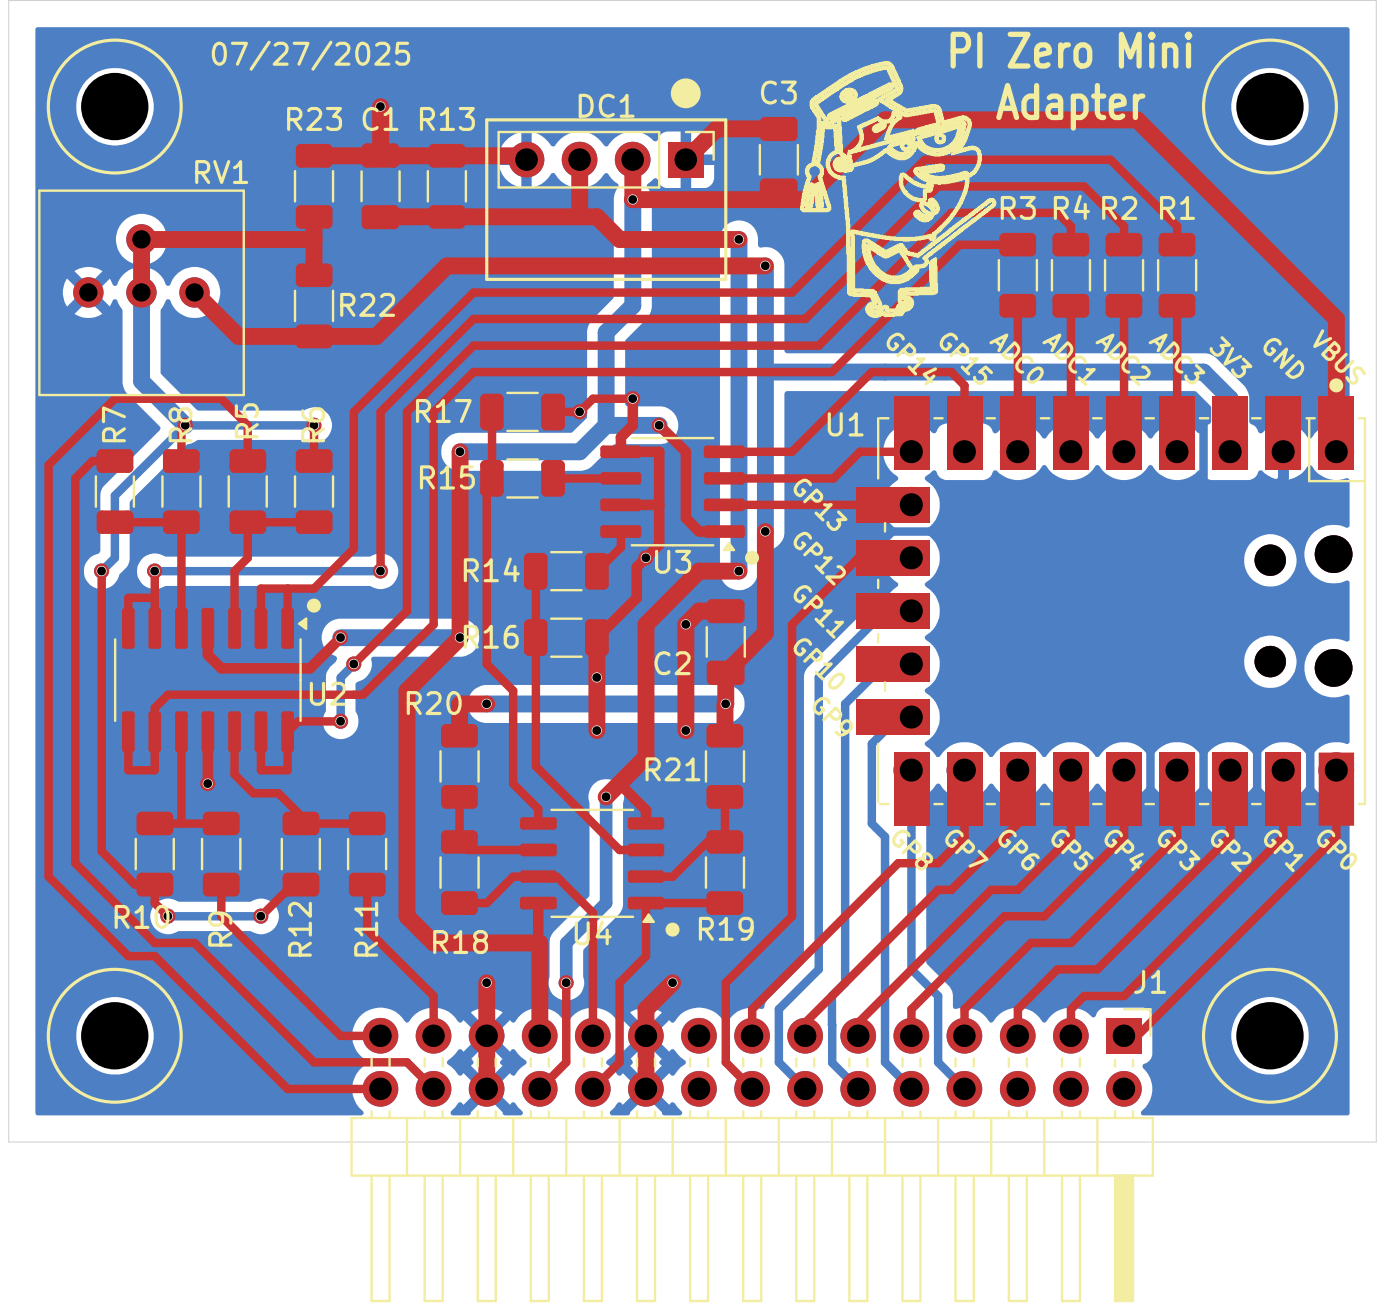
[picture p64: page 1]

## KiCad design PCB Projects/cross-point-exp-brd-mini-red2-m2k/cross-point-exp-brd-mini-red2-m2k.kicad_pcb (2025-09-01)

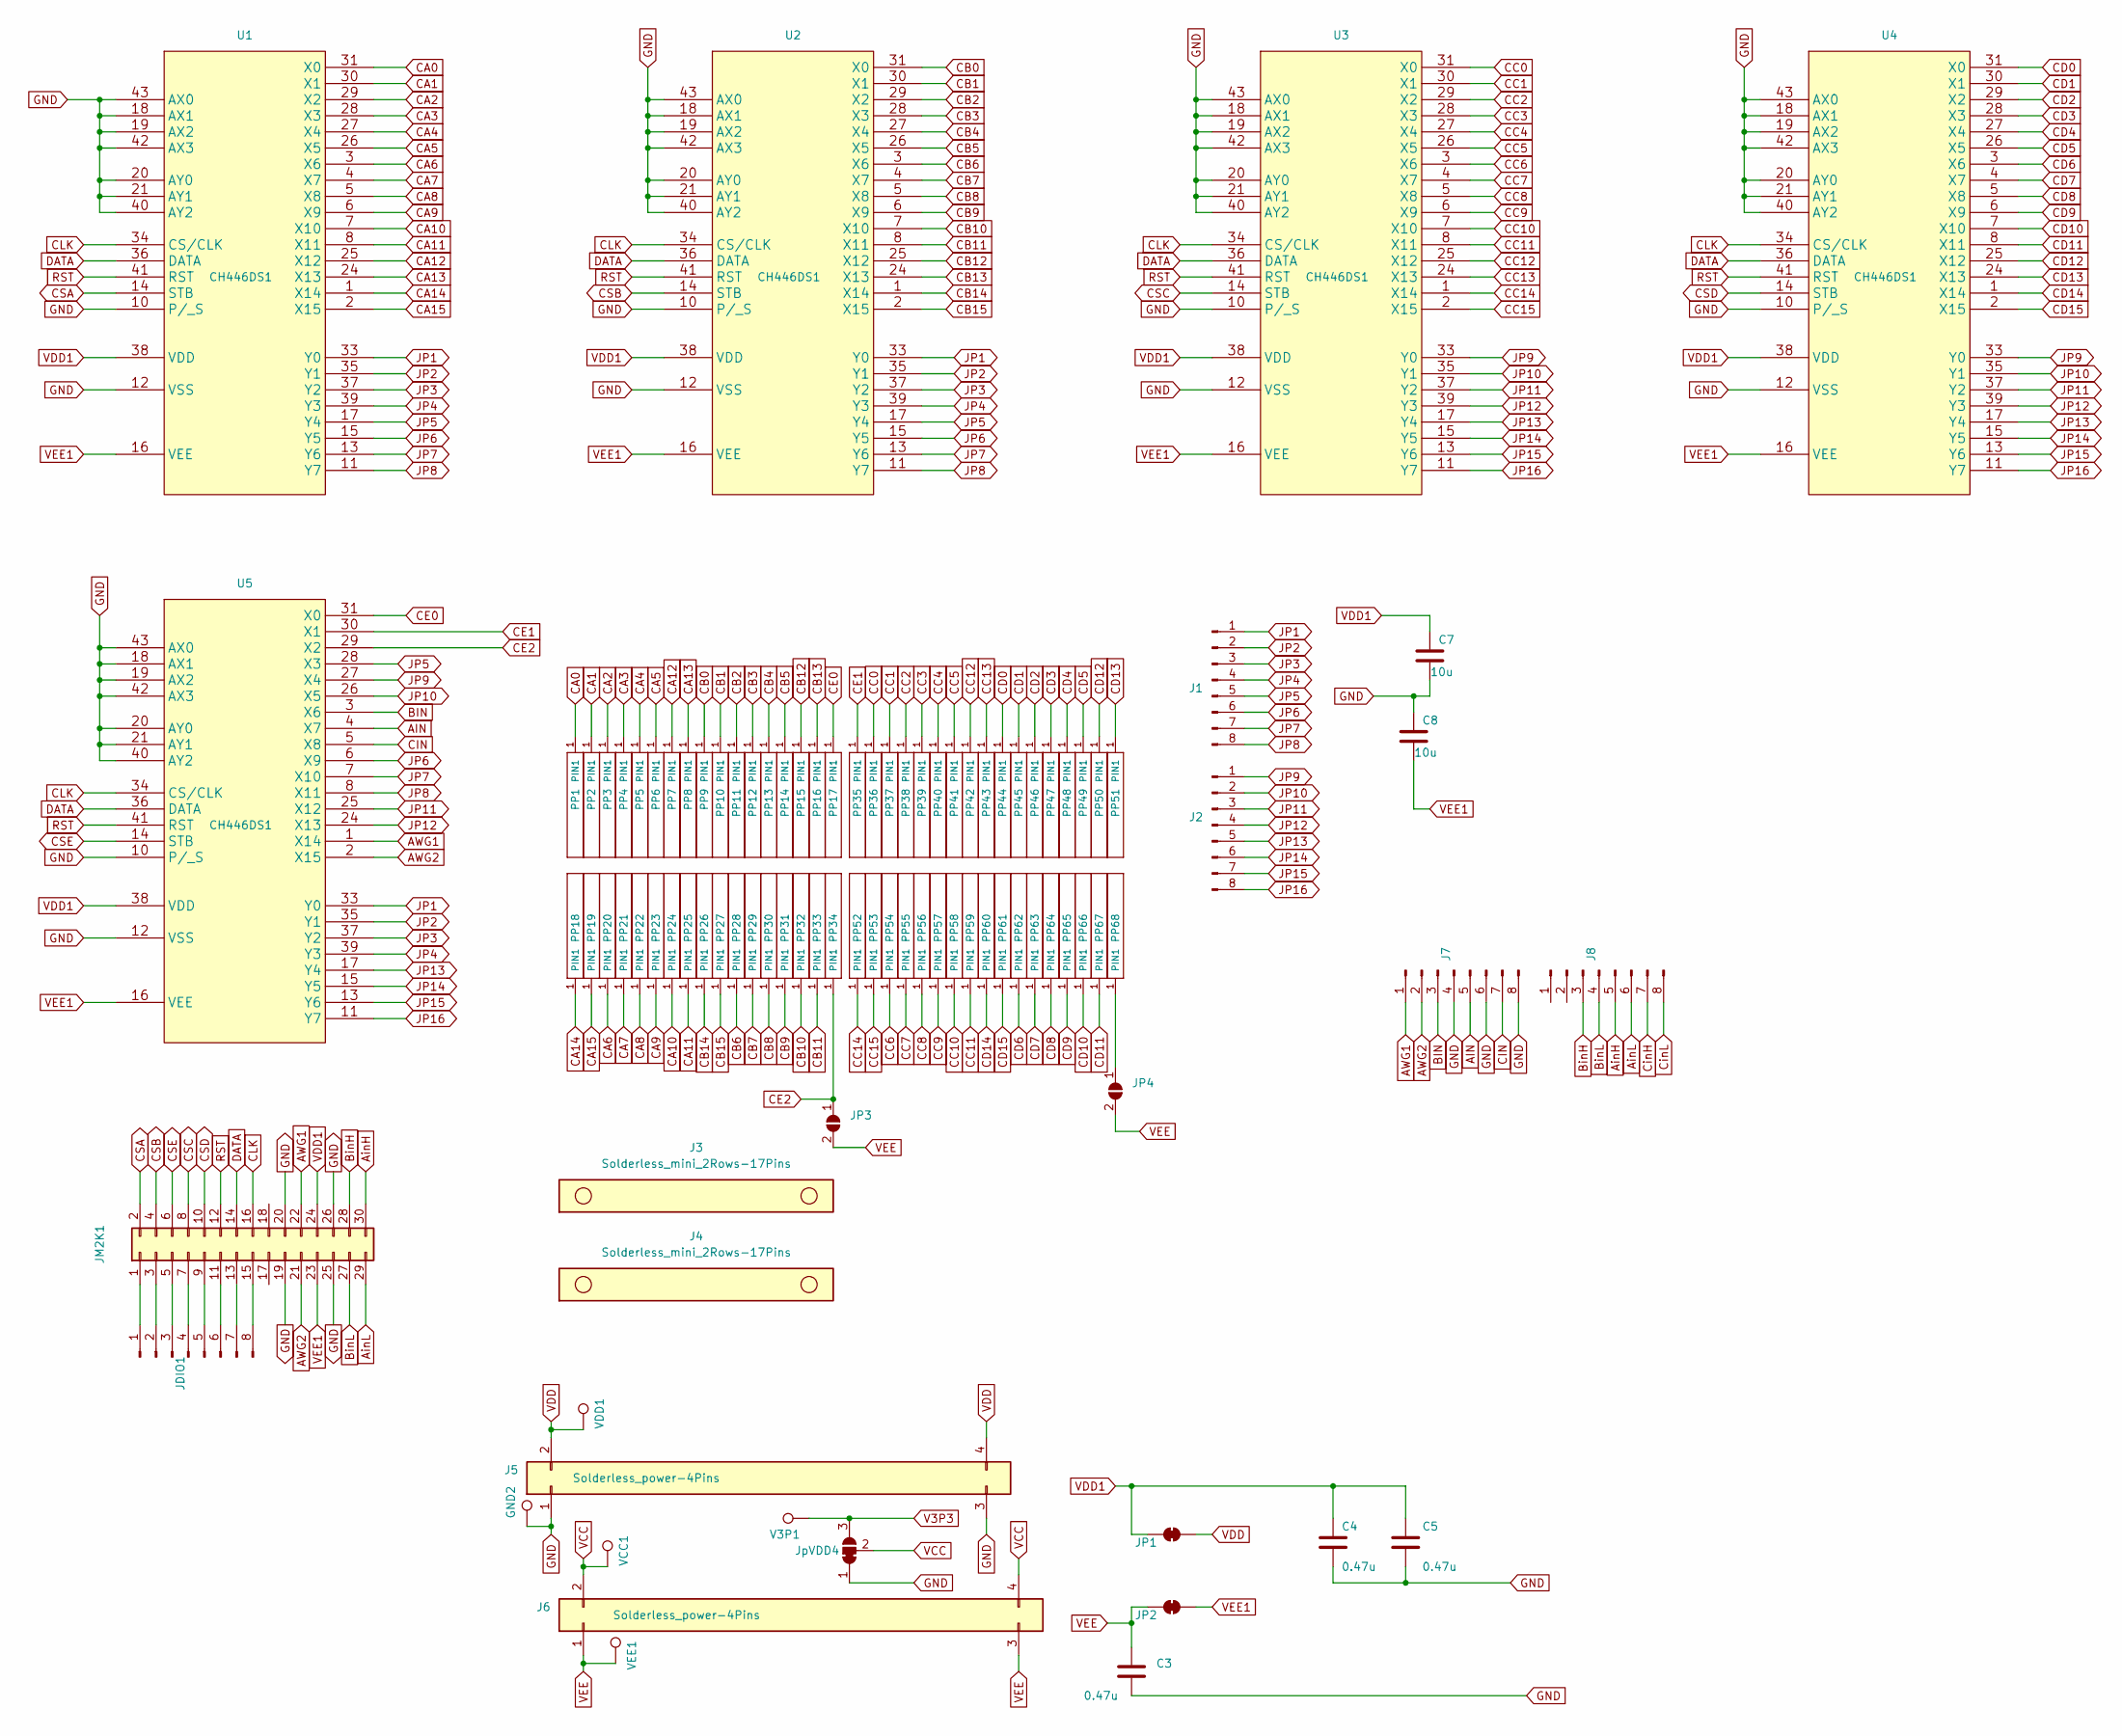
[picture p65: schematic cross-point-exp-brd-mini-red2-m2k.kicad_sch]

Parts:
C3, C4, C5: 0.47u; C_1206_3216Metric
C7, C8: 10u; C_1206_3216Metric
GND2: TestPoint; TestPoint_THTPad_D2.0mm_Drill1.0mm
J1, J2, J7, J8: Conn_01x08_Pin; PinHeader_1x08_P2.54mm_Vertical
J3, J4: Solderless_mini_2Rows-17Pins; Solderless_mini_mount_holes_2x17_P2.54mm
J5, J6: Solderless_power-4Pins; Solderless_power_2x4_P2.54mm
JDIO1: Conn_01x08_Pin; PinHeader_1x08_P2.54mm_Vertical
JM2K1: Conn_02x15_Odd_Even; PinHeader_2x15_P2.54mm_Vertical
JP1, JP2: SolderJumper_2_Bridged; SolderJumper-2_P1.3mm_Bridged_RoundedPad1.0x1.5mm
JP3, JP4: SolderJumper_2_Open; SolderJumper-2_P1.3mm_Open_RoundedPad1.0x1.5mm
JpVDD4: Conn_01x03_Pin; SolderJumper-3_P1.3mm_Bridged12_RoundedPad1.0x1.5mm_NumberL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
PP1, PP2, PP3, PP4, PP5, PP6, PP7, PP8, PP9, PP10, PP11, PP12, PP13, PP14, PP15, PP16, PP17, PP18, PP19, PP20, PP21, PP22, PP23, PP24, PP25, PP26, PP27, PP28, PP29, PP30, PP31, PP32, PP33, PP34, PP35, PP36, PP37, PP38, PP39, PP40, PP41, PP42, PP43, PP44, PP45, PP46, PP47, PP48, PP49, PP50, PP51, PP52, PP53, PP54, PP55, PP56, PP57, PP58, PP59, PP60, PP61, PP62, PP63, PP64, PP65, PP66, PP67, PP68: POGO_PIN_01X01_70-9150; MF_Connectors-POGO_PIN_70-9150
U1, U2, U3, U4, U5: CH446DS1; LQFP44_Tight
V3P1: TestPoint; TestPoint_THTPad_D2.0mm_Drill1.0mm
VCC1: TestPoint; TestPoint_THTPad_D2.0mm_Drill1.0mm
VDD1: TestPoint; TestPoint_THTPad_D2.0mm_Drill1.0mm
VEE1: TestPoint; TestPoint_THTPad_D2.0mm_Drill1.0mm

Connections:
AIN: J7.5, U5.4 (X7)
AWG1: J7.1, JM2K1.22, U5.1 (X14)
AWG2: J7.2, JM2K1.21, U5.2 (X15)
AinH: J8.5, JM2K1.30
AinL: J8.6, JM2K1.29
BIN: J7.3, U5.3 (X6)
BinH: J8.3, JM2K1.28
BinL: J8.4, JM2K1.27
CA0: PP1.1 (PIN1), U1.31 (X0)
CA1: PP2.1 (PIN1), U1.30 (X1)
CA2: PP3.1 (PIN1), U1.29 (X2)
CA3: PP4.1 (PIN1), U1.28 (X3)
CA4: PP5.1 (PIN1), U1.27 (X4)
CA5: PP6.1 (PIN1), U1.26 (X5)
CA6: PP20.1 (PIN1), U1.3 (X6)
CA7: PP21.1 (PIN1), U1.4 (X7)
CA8: PP22.1 (PIN1), U1.5 (X8)
CA9: PP23.1 (PIN1), U1.6 (X9)
CA10: PP24.1 (PIN1), U1.7 (X10)
CA11: PP25.1 (PIN1), U1.8 (X11)
CA12: PP7.1 (PIN1), U1.25 (X12)
CA13: PP8.1 (PIN1), U1.24 (X13)
CA14: PP18.1 (PIN1), U1.1 (X14)
CA15: PP19.1 (PIN1), U1.2 (X15)
CB0: PP9.1 (PIN1), U2.31 (X0)
CB1: PP10.1 (PIN1), U2.30 (X1)
CB2: PP11.1 (PIN1), U2.29 (X2)
CB3: PP12.1 (PIN1), U2.28 (X3)
CB4: PP13.1 (PIN1), U2.27 (X4)
CB5: PP14.1 (PIN1), U2.26 (X5)
CB6: PP28.1 (PIN1), U2.3 (X6)
CB7: PP29.1 (PIN1), U2.4 (X7)
CB8: PP30.1 (PIN1), U2.5 (X8)
CB9: PP31.1 (PIN1), U2.6 (X9)
CB10: PP32.1 (PIN1), U2.7 (X10)
CB11: PP33.1 (PIN1), U2.8 (X11)
CB12: PP15.1 (PIN1), U2.25 (X12)
CB13: PP16.1 (PIN1), U2.24 (X13)
CB14: PP26.1 (PIN1), U2.1 (X14)
CB15: PP27.1 (PIN1), U2.2 (X15)
CC0: PP36.1 (PIN1), U3.31 (X0)
CC1: PP37.1 (PIN1), U3.30 (X1)
CC2: PP38.1 (PIN1), U3.29 (X2)
CC3: PP39.1 (PIN1), U3.28 (X3)
CC4: PP40.1 (PIN1), U3.27 (X4)
CC5: PP41.1 (PIN1), U3.26 (X5)
CC6: PP54.1 (PIN1), U3.3 (X6)
CC7: PP55.1 (PIN1), U3.4 (X7)
CC8: PP56.1 (PIN1), U3.5 (X8)
CC9: PP57.1 (PIN1), U3.6 (X9)
CC10: PP58.1 (PIN1), U3.7 (X10)
CC11: PP59.1 (PIN1), U3.8 (X11)
CC12: PP42.1 (PIN1), U3.25 (X12)
CC13: PP43.1 (PIN1), U3.24 (X13)
CC14: PP52.1 (PIN1), U3.1 (X14)
CC15: PP53.1 (PIN1), U3.2 (X15)
CD0: PP44.1 (PIN1), U4.31 (X0)
CD1: PP45.1 (PIN1), U4.30 (X1)
CD2: PP46.1 (PIN1), U4.29 (X2)
CD3: PP47.1 (PIN1), U4.28 (X3)
CD4: PP48.1 (PIN1), U4.27 (X4)
CD5: PP49.1 (PIN1), U4.26 (X5)
CD6: PP62.1 (PIN1), U4.3 (X6)
CD7: PP63.1 (PIN1), U4.4 (X7)
CD8: PP64.1 (PIN1), U4.5 (X8)
CD9: PP65.1 (PIN1), U4.6 (X9)
CD10: PP66.1 (PIN1), U4.7 (X10)
CD11: PP67.1 (PIN1), U4.8 (X11)
CD12: PP50.1 (PIN1), U4.25 (X12)
CD13: PP51.1 (PIN1), U4.24 (X13)
CD14: PP60.1 (PIN1), U4.1 (X14)
CD15: PP61.1 (PIN1), U4.2 (X15)
CE0: PP17.1 (PIN1), U5.31 (X0)
CE1: PP35.1 (PIN1), U5.30 (X1)
CE2: JP3.1 (A), PP34.1 (PIN1), U5.29 (X2)
CIN: J7.7, U5.5 (X8)
CLK: JM2K1.16, U1.34 (CS/CLK), U2.34 (CS/CLK), U3.34 (CS/CLK), U4.34 (CS/CLK), U5.34 (CS/CLK)
CSA: JM2K1.2, U1.14 (STB)
CSB: JM2K1.4, U2.14 (STB)
CSC: JM2K1.8, U3.14 (STB)
CSD: JM2K1.10, U4.14 (STB)
CSE: JM2K1.6, U5.14 (STB)
CinH: J8.7
CinL: J8.8
DATA: JM2K1.14, U1.36 (DATA), U2.36 (DATA), U3.36 (DATA), U4.36 (DATA), U5.36 (DATA)
GND: C3.2, C4.2, C5.2, C7.2, C8.1, GND2.1, J5.1, J5.3, J7.4, J7.6, J7.8, JM2K1.19, JM2K1.20, JM2K1.25, JM2K1.26, JpVDD4.1 (A), U1.10 (P/_S), U1.12 (VSS), U1.18 (AX1), U1.19 (AX2), U1.20 (AY0), U1.21 (AY1), U1.40 (AY2), U1.42 (AX3), U1.43 (AX0), U2.10 (P/_S), U2.12 (VSS), U2.18 (AX1), U2.19 (AX2), U2.20 (AY0), U2.21 (AY1), U2.40 (AY2), U2.42 (AX3), U2.43 (AX0), U3.10 (P/_S), U3.12 (VSS), U3.18 (AX1), U3.19 (AX2), U3.20 (AY0), U3.21 (AY1), U3.40 (AY2), U3.42 (AX3), U3.43 (AX0), U4.10 (P/_S), U4.12 (VSS), U4.18 (AX1), U4.19 (AX2), U4.20 (AY0), U4.21 (AY1), U4.40 (AY2), U4.42 (AX3), U4.43 (AX0), U5.10 (P/_S), U5.12 (VSS), U5.18 (AX1), U5.19 (AX2), U5.20 (AY0), U5.21 (AY1), U5.40 (AY2), U5.42 (AX3), U5.43 (AX0); also elsewhere on the board
JP1: J1.1, U1.33 (Y0), U2.33 (Y0), U5.33 (Y0)
JP2: J1.2, U1.35 (Y1), U2.35 (Y1), U5.35 (Y1)
JP3: J1.3, U1.37 (Y2), U2.37 (Y2), U5.37 (Y2)
JP4: J1.4, U1.39 (Y3), U2.39 (Y3), U5.39 (Y3)
JP5: J1.5, U1.17 (Y4), U2.17 (Y4), U5.28 (X3)
JP6: J1.6, U1.15 (Y5), U2.15 (Y5), U5.6 (X9)
JP7: J1.7, U1.13 (Y6), U2.13 (Y6), U5.7 (X10)
JP8: J1.8, U1.11 (Y7), U2.11 (Y7), U5.8 (X11)
JP9: J2.1, U3.33 (Y0), U4.33 (Y0), U5.27 (X4)
JP10: J2.2, U3.35 (Y1), U4.35 (Y1), U5.26 (X5)
JP11: J2.3, U3.37 (Y2), U4.37 (Y2), U5.25 (X12)
JP12: J2.4, U3.39 (Y3), U4.39 (Y3), U5.24 (X13)
JP13: J2.5, U3.17 (Y4), U4.17 (Y4), U5.17 (Y4)
JP14: J2.6, U3.15 (Y5), U4.15 (Y5), U5.15 (Y5)
JP15: J2.7, U3.13 (Y6), U4.13 (Y6), U5.13 (Y6)
JP16: J2.8, U3.11 (Y7), U4.11 (Y7), U5.11 (Y7)
unnamed: JDIO1.1, JM2K1.1
unnamed: JDIO1.2, JM2K1.3
unnamed: JDIO1.3, JM2K1.5
unnamed: JDIO1.4, JM2K1.7
unnamed: JDIO1.5, JM2K1.9
unnamed: JDIO1.6, JM2K1.11
unnamed: JDIO1.7, JM2K1.13
unnamed: JDIO1.8, JM2K1.15
unnamed: JP4.1 (A), PP68.1 (PIN1)
RST: JM2K1.12, U1.41 (RST), U2.41 (RST), U3.41 (RST), U4.41 (RST), U5.41 (RST)
V3P3: JpVDD4.3 (B), V3P1.1
VCC: J6.2, J6.4, JpVDD4.2 (C), VCC1.1
VDD: J5.2, J5.4, JP1.1 (A), VDD1.1
VDD1: C4.1, C5.1, C7.1, JM2K1.24, JP1.2 (B), U1.38 (VDD), U2.38 (VDD), U3.38 (VDD), U4.38 (VDD), U5.38 (VDD)
VEE: C3.1, J6.1, J6.3, JP2.2 (B), JP3.2 (B), JP4.2 (B), VEE1.1
VEE1: C8.2, JM2K1.23, JP2.1 (A), U1.16 (VEE), U2.16 (VEE), U3.16 (VEE), U4.16 (VEE), U5.16 (VEE)

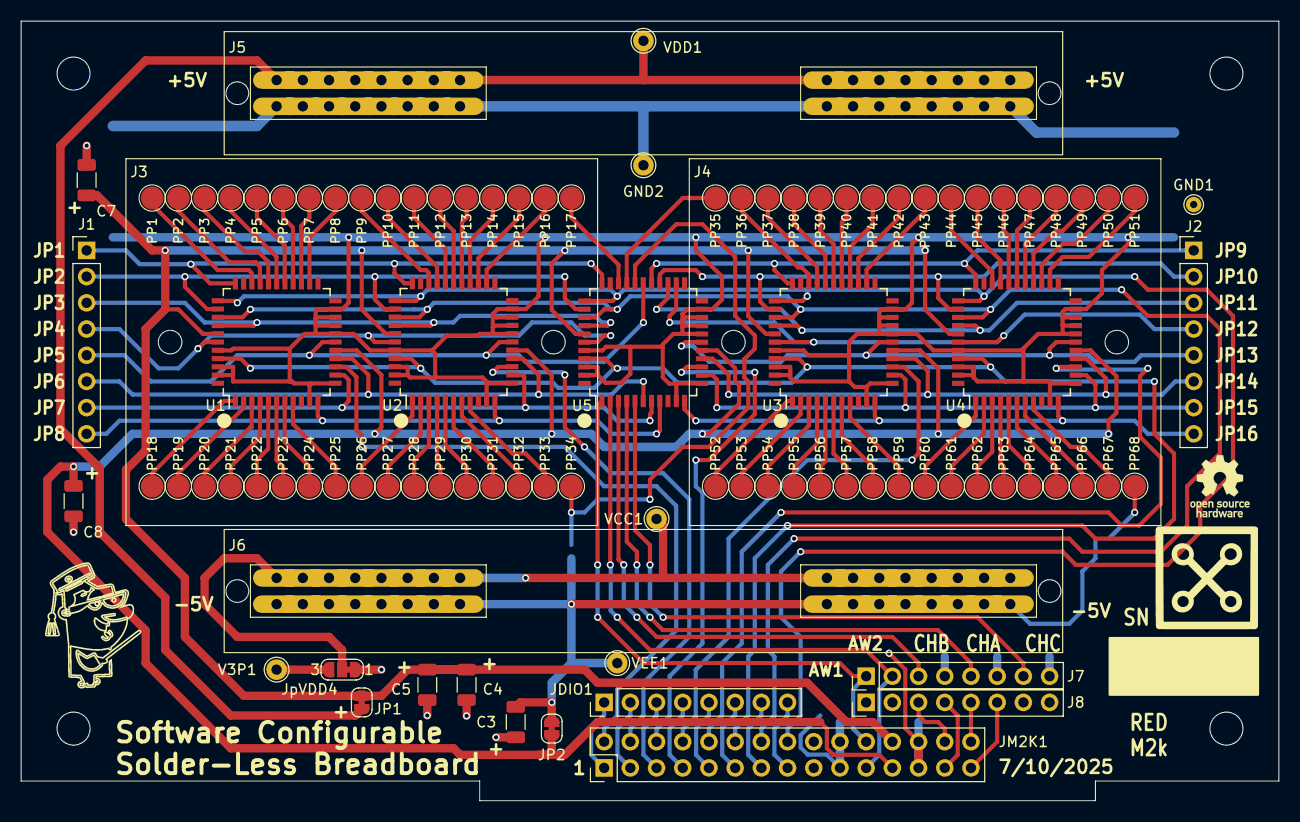
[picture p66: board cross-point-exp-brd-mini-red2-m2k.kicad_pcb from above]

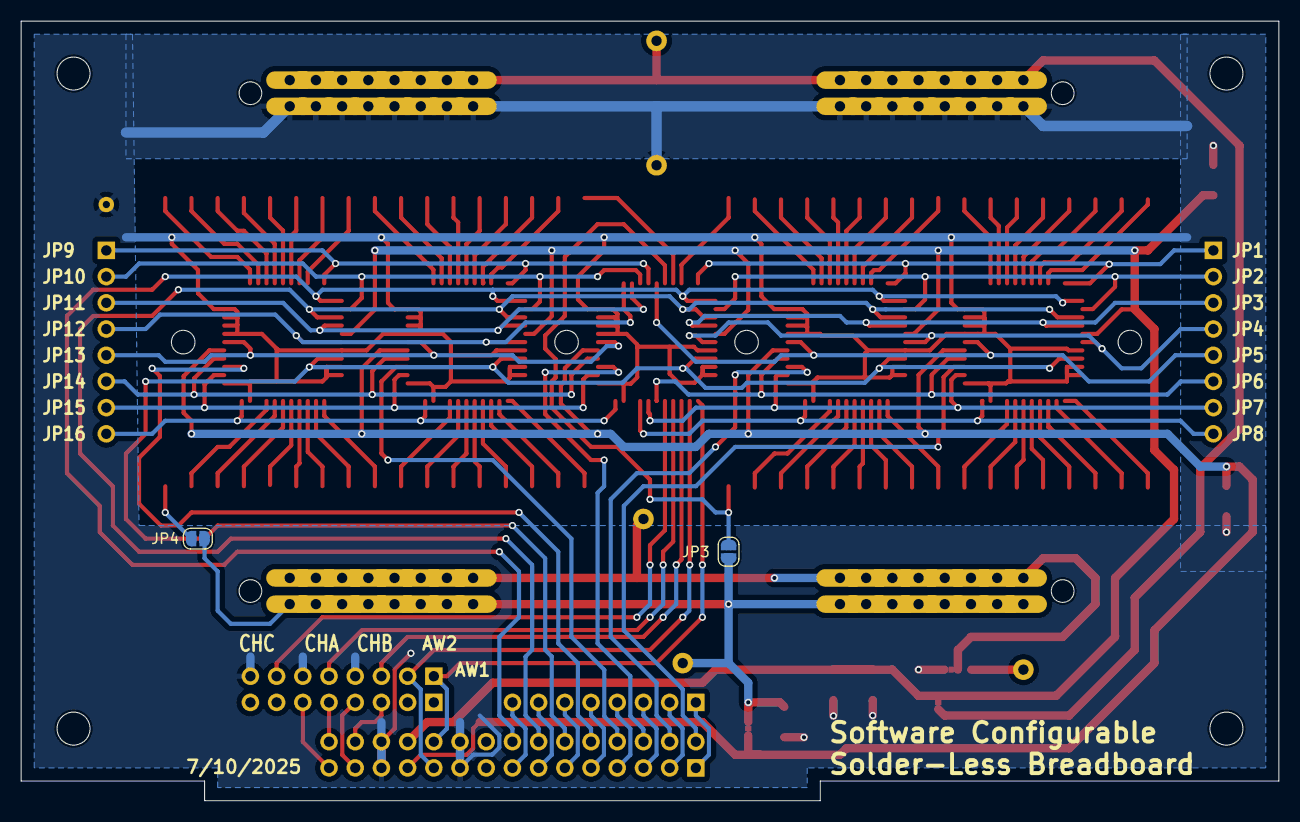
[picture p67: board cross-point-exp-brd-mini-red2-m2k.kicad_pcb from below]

Board: 2 copper layers, 121.9 x 75.6 mm, 99 parts (2 on the bottom side), 116 nets.

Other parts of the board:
GND1: TestPoint; TestPoint_THTPad_D1.5mm_Drill0.7mm

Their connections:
GND: GND1.1; also elsewhere on the board

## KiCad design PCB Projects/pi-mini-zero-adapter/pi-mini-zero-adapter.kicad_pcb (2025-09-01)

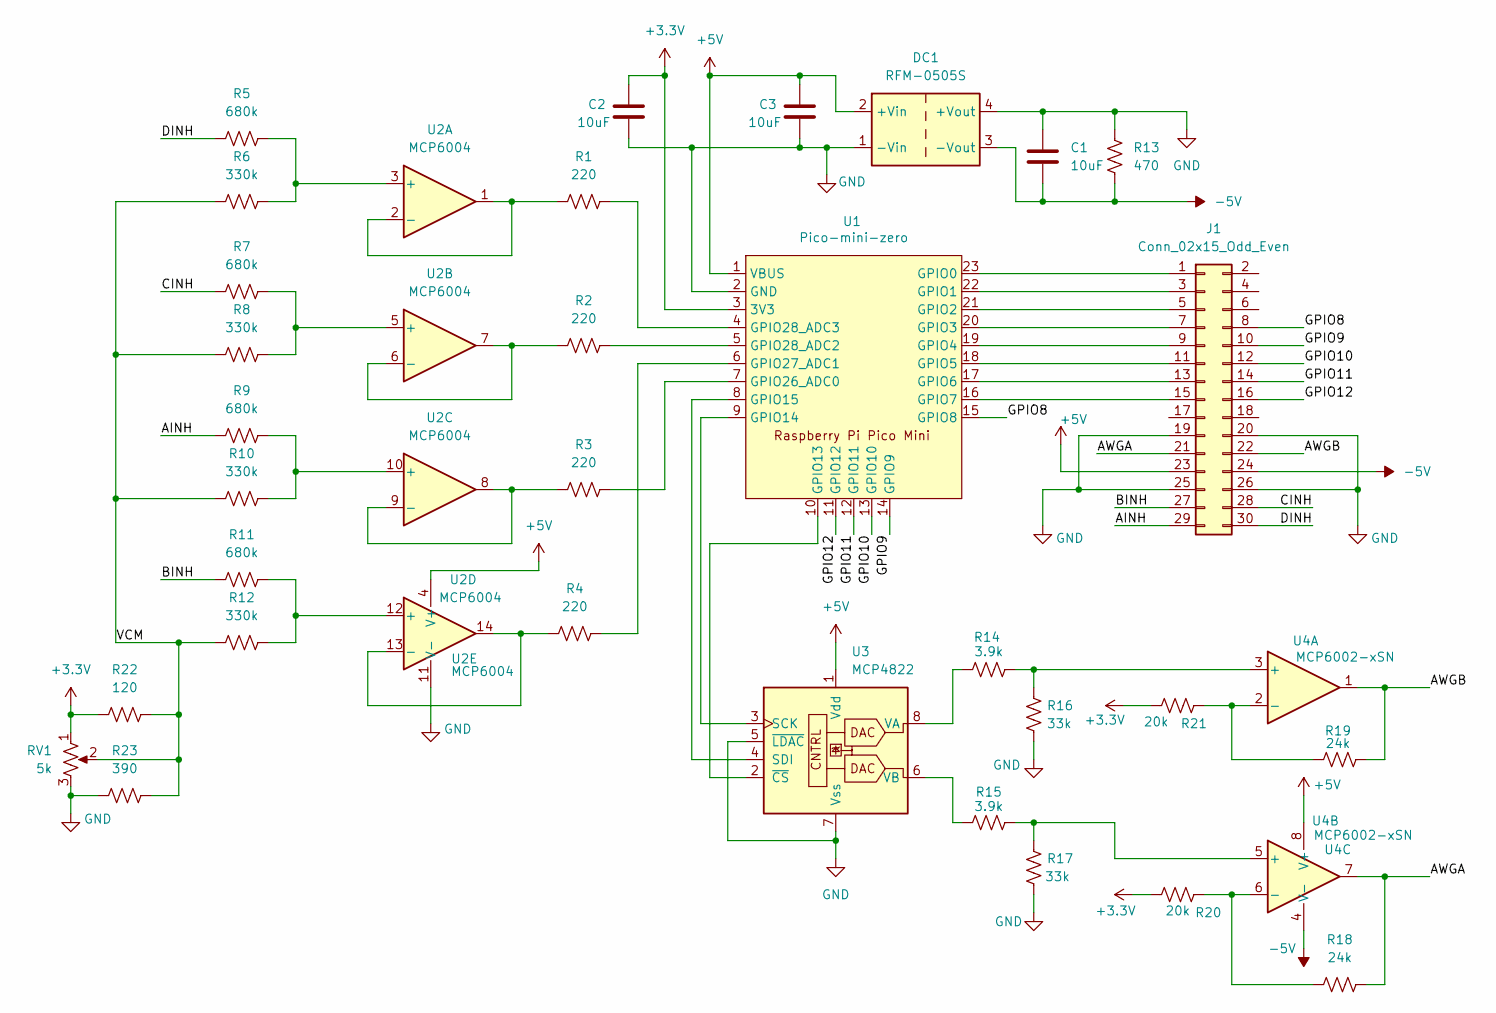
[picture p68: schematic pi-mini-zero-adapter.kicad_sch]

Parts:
C1, C2, C3: 10uF; C_1206_3216Metric
DC1: RFM-0505S
J1: Conn_02x15_Odd_Even; PinHeader_2x15_P2.54mm_Horizontal
R1, R2, R3, R4: 220; R_1206_3216Metric
R5, R7, R9, R11: 680k; R_1206_3216Metric
R6, R8, R10, R12: 330k; R_1206_3216Metric
R13: 470; R_1206_3216Metric
R14, R15: 3.9k; R_1206_3216Metric
R16, R17: 33k; R_1206_3216Metric
R18, R19: 24k; R_1206_3216Metric
R20, R21: 20k; R_1206_3216Metric
R22: 120; R_1206_3216Metric
R23: 390; R_1206_3216Metric
RV1: 5k; Potentiometer_Bourns_3386P_Vertical
U1: Pico-mini-zero; RPi_Mini_Zero_SMD_TH
U2: MCP6004; SOIC-14_3.9x8.7mm_P1.27mm
U3: MCP4822; SOIC-8_3.9x4.9mm_P1.27mm
U4: MCP6002-xSN; SO-8_3.9x4.9mm_P1.27mm

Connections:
+3.3V: C2.1, R20.2, R21.2, R22.2, RV1.1, U1.3 (3V3)
+5V: C3.1, DC1.2 (+Vin), J1.23, U1.1 (VBUS), U2.4 (V+), U3.1 (Vdd), U4.8 (V+)
-5V: C1.2, DC1.3 (-Vout), J1.24, R13.2, U4.4 (V-)
/AINH: J1.29, R9.2
/AWGA: J1.21, R18.1, U4.7
/AWGB: J1.22, R19.1, U4.1
/BINH: J1.27, R11.2
/CINH: J1.28, R7.2
/DINH: J1.30, R5.2
/GPIO8: J1.8, U1.15 (GPIO8)
/GPIO9: J1.10, U1.14 (GPIO9)
/GPIO10: J1.12, U1.13 (GPIO10)
/GPIO11: J1.14, U1.12 (GPIO11)
/GPIO12: J1.16, U1.11 (GPIO12)
/VCM: R6.2, R8.2, R10.2, R12.2, R22.1, R23.1, RV1.2
GND: C1.1, C2.2, C3.2, DC1.1 (-Vin), DC1.4 (+Vout), J1.19, J1.20, J1.25, J1.26, R13.1, R16.1, R17.1, R23.2, RV1.3, U1.2 (GND), U2.11 (V-), U3.5 (~LDAC), U3.7 (Vss)
unnamed: J1.1, U1.23 (GPIO0)
unnamed: J1.3, U1.22 (GPIO1)
unnamed: J1.5, U1.21 (GPIO2)
unnamed: J1.7, U1.20 (GPIO3)
unnamed: J1.9, U1.19 (GPIO4)
unnamed: J1.11, U1.18 (GPIO5)
unnamed: J1.13, U1.17 (GPIO6)
unnamed: J1.15, U1.16 (GPIO7)
unnamed: U1.10 (GPIO13), U3.2 (~CS)
unnamed: U1.9 (GPIO14), U3.3 (SCK)
unnamed: U1.8 (GPIO15), U3.4 (SDI)
unnamed: R3.1, U1.7 (GPIO26_ADC0)
unnamed: R4.1, U1.6 (GPIO27_ADC1)
unnamed: R2.1, U1.5 (GPIO28_ADC2)
unnamed: R1.1, U1.4 (GPIO28_ADC3)
unnamed: R5.1, R6.1, U2.3 (+)
unnamed: R1.2, U2.1, U2.2 (-)
unnamed: R7.1, R8.1, U2.5 (+)
unnamed: R2.2, U2.6 (-), U2.7
unnamed: R9.1, R10.1, U2.10 (+)
unnamed: R3.2, U2.8, U2.9 (-)
unnamed: R11.1, R12.1, U2.12 (+)
unnamed: R4.2, U2.13 (-), U2.14
unnamed: R14.2, U3.8 (VA)
unnamed: R15.2, U3.6 (VB)
unnamed: R14.1, R16.2, U4.3 (+)
unnamed: R19.2, R21.1, U4.2 (-)
unnamed: R15.1, R17.2, U4.5 (+)
unnamed: R18.2, R20.1, U4.6 (-)

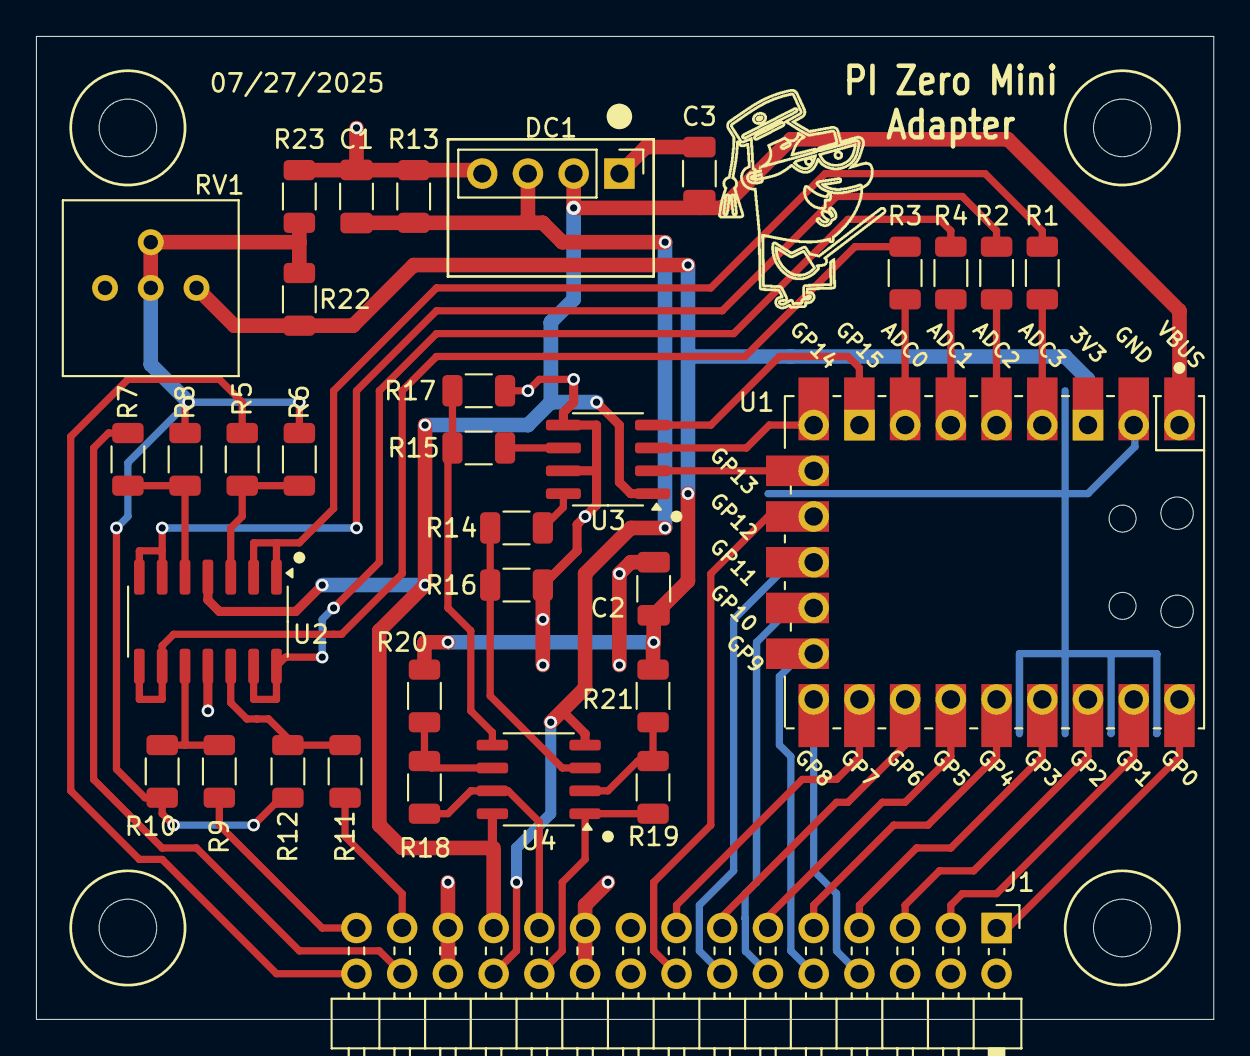
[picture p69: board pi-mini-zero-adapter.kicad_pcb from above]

Board: 2 copper layers, 65.4 x 54.6 mm, 33 parts (0 on the bottom side), 45 nets.

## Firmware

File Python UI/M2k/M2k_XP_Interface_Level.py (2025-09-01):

#
# Hardware specific interface functions
# For ADALM2000 aka M2k and Red M2k XPoint breadboards (8-1-2025)
# Written using Python version 3.10, Windows OS 
#
try:
    import serial
    import serial.tools.list_ports
except:
    root.update()
    showwarning("WARNING","Serial Library not installed?!")
    root.destroy()
    exit()
try:
    import libm2k
    libm2k_found = True
except:
    root.update()
    showwarning("WARNING","libm2k not installed?!")
    root.destroy()
    exit()
#
ConfigFileName = "alice-last-config.cfg"
Tdiv.set(10)
ZeroGrid.set(0)
TimeDiv = 0.002

#
# adjust for your specific hardware by changing these values
DevID = "M2k"
TimeSpan = 0.001
CHANNELS = 2 # Number of supported Analog input channels
AWGChannels = 2 # Number of supported Analog output channels
PWMChannels = 0 # Number of supported PWM output channels
DigChannels = 0 # Number of supported Dig channels
LogicChannels = 0 # Number of supported Logic Analyzer channels
EnablePGAGain = 0 # 1
EnableOhmMeter = 0
EnableDmmMeter = 0
EnableDigIO = 0
UseSoftwareTrigger = 1 # use software triggering for now
AllowFlashFirmware = 0
SaveDig = 0
InterpRate = 1
MaxSamples = 8192
SMPfft = MaxSamples # Set FFT size based on fixed acquisition record length
MatrixStatus = IntVar()
MatrixStatus.set(0)
AWGBuffLen = 1024
AWGPeakToPeak = 10.0 # Iternal reference voltage for MCP4822
AWGRes = 4095 # For 8 bits, 4095 for 12 bits, 1023 for 10 bits
ATmin = 8 # set minimum DAC update rate to 8 uSec
MaxAWGSampleRate = 750000 # set to 1 / 8 uSec
AWGSampleRate = MaxAWGSampleRate
TriggerChannel = "CH1"
TriggerEdge = "RISE"
Wait = 0.001
PlusUSEnab = IntVar()
PlusUSEnab.set(1)
NegUSEnab = IntVar()
NegUSEnab.set(1)
## Time list in s/div
TMpdiv = ("0.1us","0.2us","0.5us","1us","2us","5us", "10us", "20us", "50us", "100us", "200us", "500us", "1.0ms", "2.0ms", "5.0ms",
          "10ms", "20ms", "50ms", "100ms", "200ms", "500ms", "1.0s", "2.0s", "5.0s")
#
OldCH1pdvRange = CH1pdvRange = 1.0
OldCH2pdvRange = CH2pdvRange = 1.0
#
AWGAwaveform = numpy.ones(1024)
AWGBwaveform = numpy.ones(1024)
#
# Breadboard pin maping for M2k Red 2 layout
#
TL1 = "CA0"; TL2 = "CA1"; TL3 = "CA2"; TL4 = "CA3"; TL5 = "CA4"; TL6 = "CA5"; TL7 = "CA12"; TL8 = "CA13"
BL1 = "CA14"; BL2 = "CA15"; BL3 = "CA6"; BL4 = "CA7"; BL5 = "CA8"; BL6 = "CA9"; BL7 = "CA10"; BL8 = "CA11"
TL9 = "CB0"; TL10 = "CB1"; TL11 = "CB2"; TL12 = "CB3"; TL13 = "CB4"; TL14 = "CB5"; TL15 = "CB12"; TL16 = "CB13"
BL9 = "CB14"; BL10 = "CB15"; BL11 = "CB6"; BL12 = "CB7"; BL13 = "CB8"; BL14 = "CB9"; BL15 = "CB10"; BL16 = "CB11"
BL17 = "CE2"; TL17 = "CE0"; TR1 = "CE1"

TR2 = "CC0"; TR3 = "CC1"; TR4 = "CC2"; TR5 = "CC3"; TR6 = "CC4"; TR7 = "CC5"; TR8 = "CC12"; TR9 = "CC13"
BR1 = "CC14"; BR2 = "CC15"; BR3 = "CC6"; BR4 = "CC7"; BR5 = "CC8"; BR6 = "CC9"; BR7 = "CC10"; BR8 = "CC11"
TR10 = "CD0"; TR11 = "CD1"; TR12 = "CD2"; TR13 = "CD3"; TR14 = "CD4"; TR15 = "CD5"; TR16 = "CD12"; TR17 = "CD13"
BR9 = "CD14"; BR10 = "CD15"; BR11 = "CD6"; BR12 = "CD7"; BR13 = "CD8"; BR14 = "CD9"; BR15 = "CD10"; BR16 = "CD11"

AINH = "CE6"; BINH = "CE7"; CINH = "CE8"
AWG1 = "CE14"; AWG2 = "CE15"
JP5 = "CE3"; JP6 = "CE9"; JP7 = "CE10"; JP8 = "CE11"
JP9 = "CE4"; JP10 = "CE5"; JP11 = "CE12"; JP12 = "CE13"
# Change these serial pins to match board layout
CSA = 7; CSB = 6; CSE = 5; CSC = 4; CSD = 3; RST = 2; DATA = 1; CLK = 0
#
JumperSpinBoxList = ("JP1", "JP2", "JP3", "JP4", "JP5", "JP6", "JP7", "JP8",
                     "JP9", "JP10", "JP11", "JP12", "JP13", "JP14", "JP15", "JP16")
CompSpinBoxList = ("AWG1", "AWG2", "AINH", "BINH", "CINH")
#
# Cross point matrix functions
#
def ReadNetlist(nfp):
#
    try: # First check if net list is UTF-16-LE
        NetList = open(nfp, 'r', encoding='utf-16-le')     
        lines = NetList.readlines()
        print("Found file as UTF-16-LE")
    except: # If fails then must beUTF-8
        NetList.close()
        NetList = open(nfp, 'r', encoding='utf-8')
        lines = NetList.readlines()
        print("Found file as UTF-8")
    NetList.close()
    # print(lines)
    # create a list of strings for all subcircuit istance lines in netlist, ignore rest
    netlist_stripped = []
    for line in lines:
        # Select only the lines that contain "cross_point"
        # print(line)
        # line = line.encode('ascii')
        # if "TL" in line[0:4] or "BL" in line[0:4] or "TR" in line[0:4] or "BR" in line[0:4]:
        if "cross_point" in line:
            netlist_stripped.append(line.split())
    return netlist_stripped
#
def WhichChip(CompPin): # determine which cross point chip is used A-E

    ChipNum = 0
    # print("Which Chip ", CompPin)
    if isinstance(CompPin, int):
        return 0
    else:
        if "CA" in CompPin:
            ChipNum = 1
        if "CB" in CompPin:
            ChipNum = 2
        if "CC" in CompPin:
            ChipNum = 3
        if "CD" in CompPin:
            ChipNum = 4
        if "CE" in CompPin:
            ChipNum = 5
        return ChipNum
##
def ConfigCrossPoint():
    global FileString, NumConn, ErrConn
    
    netlist = FileString.get()
    ComponentList = ReadNetlist(netlist) # list of all subcircuit instances found
    CompNum = len(ComponentList) # number of subcircuits
    index = 0
    connects = 0
    Errors = 0
    ErrorString = ""
    ResetMatrix() # Reset all cross point switches to open
    time.sleep(0.01)
    while index < CompNum:
        CompPins = ComponentList[index]
        index = index + 1
        if "JP" in CompPins[1]:
            Jumper = CompPins[1] # First net is Jumper bus
            JmpNum = int(Jumper.replace("JP","")) - 1 # extract number 0-15
            try:
                XPin = eval(CompPins[2]) # is Second net a component BB pin
                xpin = CompPins[2]
                xpin = xpin.replace("X","")
                xpin = xpin.replace(chr(167),"")# remove §
            except:
                # for case where synbol instance name is the BB pin 
                xpin = CompPins[0]
                xpin = xpin.replace("X","")
                xpin = xpin.replace(chr(167),"")# remove §
                XPin = eval(xpin)
            #
            if XPin == 0: # cross point connected to node 0?
                xpin = CompPins[0]
                xpin = xpin.replace("X","")
                xpin = xpin.replace(chr(167),"")# remove §
                XPin = eval(xpin)
                # print(XPin,xpin)
            if "L" in xpin:
                if xpin != "TL17":
                    if JmpNum > 7:
                        ErrorString = "Jumper out of range in " + str(CompPins)
                        print(ErrorString)
                        Errors = Errors + 1
                        continue
                else: # BB pin TL17 can connect to any of JP1-4 and JP13-16
                    if JmpNum > 3 and JmpNum < 12:
                        ErrorString = "Jumper out of range in " + str(CompPins)
                        print(ErrorString)
                        Errors = Errors + 1
                        continue
                    if JmpNum > 7:
                        JmpNum = JmpNum - 8
                    # print(xpin, XPin, JmpNum)
            elif "R" in xpin:
                if xpin != "TR1":
                    if JmpNum < 7 or JmpNum > 15:
                        ErrorString = "Jumper out of range in " + str(CompPins)
                        print(ErrorString)
                        Errors = Errors + 1
                        continue
                    JmpNum = JmpNum - 8
                else: # BB pin TR1 can connect to any of JP1-4 and JP13-16
                    if JmpNum > 3 and JmpNum < 12:
                        ErrorString = "Jumper out of range in " + str(CompPins)
                        print(ErrorString)
                        Errors = Errors + 1
                        continue
                    if JmpNum > 7:
                        JmpNum = JmpNum - 8
            #
            ChipNum = WhichChip(XPin) # Find which switch chip 1-5
            if ChipNum == 5 and JmpNum > 7:
                JmpNum = JmpNum - 8
            if ChipNum > 0:
                CmpNum = int(only_numerics(XPin)) # extract number 0-15
                SendToMatrix(JmpNum, CmpNum, ChipNum, 1)
                connects = connects + 1
            else:
                ErrorString = "Error Unknown switch chip number for? " + str(xpin)
                print(ErrorString)
                # print(CompPins)
                # print(XPin,xpin)
                Errors = Errors + 1
    NumConn.config(text = "Number of connections = " + str(connects) + " Errors = " + str(Errors))
    if Errors > 0:
        ErrConn.config(text = ErrorString )
    #print("Number of connections ", connects)
##
#
def ResetMatrix():
    global CSA, CSB, CSC, CSD, CSE, CLK, RST, DATA
    # Reset all cross point switches to off
    dig.setValueRaw(RST, 1) # Toggel Reset pin High
    # Wait
    dig.setValueRaw(RST, 0) # Toggel Reset pin Low
    time.sleep(0.001) # Reset all cross point switches to open
##
def BrowsNetFile():
    global FileString, NetList
    
    NetList = askopenfilename(defaultextension = ".cir", filetypes=[("Net List files", ".cir .net")])
    FileString.delete(0,"end")
    FileString.insert(0,NetList)
##
def ManualReturn(event):

    ManualMartix()
##
def ManualMartix():
    global CompString, JumperString, OnOffString, NumConn

    Errors = 0
    Jumper = JumperString.get()
    JmpNum = int(Jumper.replace("JP","")) - 1 # extract number 0-15
    CompPin = CompString.get()
    if "JP" in Jumper:
        if "L" in CompPin:
            if CompPin != "TL17":
                if JmpNum > 7:
                    print("Jumper out of range in " , CompPin)
                    Errors = Errors + 1
            else: # BB pin TL17 can connect to any of JP1-4 and JP13-16
                if JmpNum > 3 and JmpNum < 12:
                    print("Jumper out of range in " , CompPin)
                    Errors = Errors + 1
                if JmpNum > 7:
                    JmpNum = JmpNum - 8
                # print(xpin, XPin, JmpNum)
        elif "R" in CompPin:
            if CompPin != "TR1":
                if JmpNum < 7 or JmpNum > 15:
                    print("Jumper out of range in " , CompPins)
                    Errors = Errors + 1
                JmpNum = JmpNum - 8
            else: # BB pin TR1 can connect to any of JP1-4 and JP13-16
                if JmpNum > 3 and JmpNum < 12:
                    print("Jumper out of range in " , CompPins)
                    Errors = Errors + 1
                if JmpNum > 7:
                    JmpNum = JmpNum - 8
        #
    #print(Jumper, CompPin)
    if Errors > 0:
        NumConn.config(text = "Error: Jumper out of range! " + str(CompPin) + " " + str(Jumper))
        return
    Xpin = eval(CompPin)
    # print(Xpin, CompPin)
    OnOff = int(OnOffString.get())
    ChipNum = WhichChip(Xpin) # Second net is Component pin
    if ChipNum == 5 and JmpNum > 7:
        JmpNum = JmpNum - 8
    if ChipNum > 0:
        CmpNum = int(only_numerics(Xpin)) # extract number 0-7
        SendToMatrix(JmpNum, CmpNum, ChipNum, OnOff)
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

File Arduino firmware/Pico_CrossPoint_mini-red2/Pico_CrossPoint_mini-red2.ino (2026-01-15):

//Pico_CrossPoint controller using mini red solderless breadboards with MCP4822 DAC
// 10/10/2025
#include "pico/stdlib.h"
#include "hardware/adc.h"
#include "hardware/pwm.h"
#include <hardware/timer.h>
#include <hardware/irq.h>
#include <SPI.h>
#include "pico/multicore.h"

#define ALARM_NUM 1
#define ALARM_IRQ TIMER_IRQ_1

uint8_t scopea[16384]; // 14336/8 ~ 1700 max samples
//  uint8_t digin[4096];
uint16_t awgouta[4096];
uint16_t awgoutb[4096];

short led = 25;
short awgona;
short awgonb;
short awgtpa;
short awgtpb;
short addr;
short data;
short awgdata;
short awgres;
short n;
short m;
short xadr = 0;
short yadr = 0;
short cadr = 1;
short dadr = 7;
short swon = 0;
uint32_t tg;
short sync = 0;
short point = 0;
float Step;
unsigned int at, at2, st, st2, stReal;
short bmax=4096;
short amax=4096;
short bs=1024;
uint16_t tbs=2048;
uint16_t rbs=3072;
uint16_t fbs=4096;
uint16_t vbs=5120;
uint16_t sbs=6144;
uint16_t ebs=7168;
uint16_t gbs=8192;
short dy=1;
uint16_t ns=1024;
uint16_t ms=1024;
int pwmf = 500;
int pwid = 500;

static void alarm_irq(void) {
  hw_clear_bits(&timer_hw->intr, 1u << ALARM_NUM);
  alarm_in_us_arm(at);
  if (awgona == 1){ // send data to DAC A
    if (n >= ns) n = 0;
    SPI.transfer16(awgouta[n]);
    n++;
  } else {
    n = 0;
  }
  if (awgonb == 1) { // send data to DAC B
    if (m >= ms) m = 0;
    SPI.transfer16(awgoutb[m]);
    m++;
  }
  else {
    m = 0;
  }
}

static void alarm_in_us_arm(uint32_t delay_us) {
  uint64_t target = timer_hw->timerawl + delay_us;
  timer_hw->alarm[ALARM_NUM] = (uint32_t) target;
}

static void alarm_in_us(uint32_t delay_us) {
  hw_set_bits(&timer_hw->inte, 1u << ALARM_NUM);
  irq_set_exclusive_handler(ALARM_IRQ, alarm_irq);
  irq_set_enabled(ALARM_IRQ, true);
  alarm_in_us_arm(at);
}

void setup1() {
  at=20;
  awgona = 0; // default AWG A off
  awgonb = 0; // default AWG B off
  alarm_in_us(at);
}

void loop1() {
  
}
  
void setup() {
  
  Serial.begin(2000000);
  pinMode(led, OUTPUT);
  pinMode(0, OUTPUT); // common Clock input 
  pinMode(1, OUTPUT); // common Data input
  pinMode(2, OUTPUT); // common Reset input
  pinMode(3, OUTPUT); // CSD strobe for switch chip D 
  pinMode(4, OUTPUT); // CSE strobe for switch chip E 
  pinMode(5, OUTPUT); // CSC strobe for switch chip C
  pinMode(6, OUTPUT); // CSB strobe for switch chip B 
  pinMode(7, OUTPUT); // CSA strobe for switch chip A
  pinMode(8, INPUT); // Aux common Clock input 
  pinMode(9, INPUT); // Aux common Data input
  pinMode(10, INPUT); // Aux common Reset input
  pinMode(11, INPUT); // AUX CSD strobe for switch chip D 
  pinMode(12, INPUT); // Aux CSC strobe for switch chip E
  pinMode(13, INPUT); // Aux CSE strobe for switch chip C
  pinMode(14, INPUT); // AUX CSB strobe for switch chip B 
  pinMode(15, INPUT); // Aux CSA strobe for switch chip A
  //
  pinMode(16, OUTPUT); // InHib for ID comp switch chip
  pinMode(22, OUTPUT); // A for ID comp switch chip
  pinMode(21, OUTPUT); // B for ID comp switch chip
  pinMode(20, OUTPUT); // C for ID comp switch chip
  // preset cross point control lines
  digitalWrite(0, HIGH); // CLK input idles High
  delayMicroseconds(6); // Wait
  digitalWrite(2, HIGH); // Toggel Reset pin High
  digitalWrite(10, HIGH); // Toggel Aux Reset pin High
  delayMicroseconds(6); // Wait
  digitalWrite(2, LOW); // Reset input defaults Low
  digitalWrite(10, LOW); // Aux Reset input defaults Low
  digitalWrite(1, LOW); // Data input defaults Low
  digitalWrite(7, LOW); // Chip A Strobe input defaults Low
  digitalWrite(6, LOW); // Chip B Strobe input defaults Low
  digitalWrite(5, LOW); // Chip C Strobe input defaults Low
  digitalWrite(3, LOW); // Chip D Strobe input defaults Low
  digitalWrite(4, LOW); // Chip E Strobe input defaults Low
//
  digitalWrite(16, HIGH); // Default InHib High to turn off all switches
  digitalWrite(22, LOW); // Sw A Low
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

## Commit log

2025-02-23 Add Assembly Videos
    Added two videos showing how to bend the power rail jumpers.
2025-04-05 Add new SMD PCB design files
    Add new KiCAD project for mostly SMD version of the board.
    [Bom_pcbgogo.xlsx, PEC11R-4215F-S0024--3DModel-STEP-56544.STEP, SSSS223600.step, WS2812C-2020_Color.step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]
2025-04-12 JLCPCB Test Run Project files
    The KiCAD project folder for the Red2 SMD pcb layout with solder jumpers now contains the JLCPCB Gerber, BOM and component placement files for board assembly at JLCPCB.
    [Bom_pcbgogo.xlsx, JLCPCB-red2-sjmp-top-pos.csv, JLCPCB_BOM_RED2_SMD.xlsx, PEC11R-4215F-S0024--3DModel-STEP-56544.STEP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]
2025-05-19 Python code updates
    Bug fixes to main ALICE code and hardware code for original through hole Red boards. Adding new hardware code for surface mound Red boards and first pass at self test function.
2025-06-03 Add PCB built instructions
    This update adds instructions to build PCBs at JLCPCB. Also improvements to Python UI and some additional example LTspice schematics.
2025-06-16 Adding LTspice examples
    Adding a number of digital LTspice example schematics and fixes to Red board python configuration files.
2025-07-18 M2k Python Code first release
    This is the first release of libm2k Pyhton code to control a cross point board.
2025-09-01 Add Rekeases
    Adds special RPI Bundle archive to Releases folder.
    [JLCPCB_BOM_ADPT.xlsx, JLCPCB_BOM_RED2_M2K.xlsx, PEC11R-4215F-S0024--3DModel-STEP-56544.STEP, SSSS223600.step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]
2026-01-15 January 2026 release of project files
    This is the January project files release ahead of Spring semester. Includes files for RED3 version of the hardware.
